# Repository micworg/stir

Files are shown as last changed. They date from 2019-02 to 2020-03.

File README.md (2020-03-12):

# Dual magnetic stir controller V2

## Overview

This is the Arduino project to build a double magnetic stirrer based on 2 fans, a 1602 LCD display, a KY-040 encoder and an Arduino Nano and a special PCB designed in the Hobbybrauer-Forum.

<p align="center">
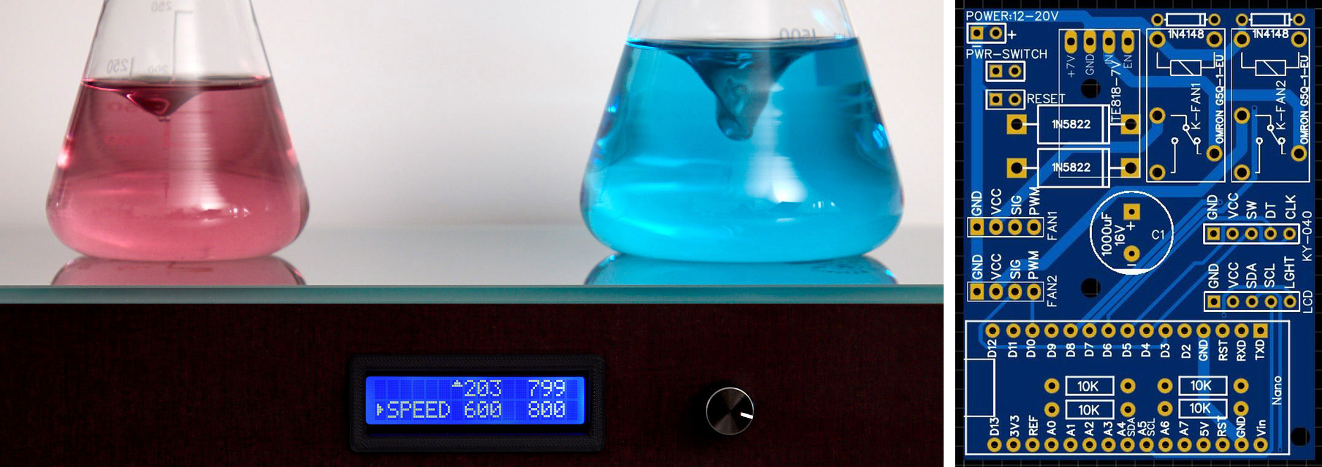
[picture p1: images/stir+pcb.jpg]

</p>

V2 supports dual voltage for the fans which increases the speed range.

In order to put the stirrer into operation you have to change the settings in stir.ino according to your setup (see below).

The stir V2 software is compatible with V1 hardware if you have used neither the RS232 Api nor the OFF0 and OFF1 relais pins.

## Part List

* 1x PCB "Stir V2.0"
* 1x Arduino Nano V3
* 1x [Voltage regulator TE818 5-24V to 5V 3A step down buck converter](https://www.ebay.de/itm/5x-Voltage-Regulator-5-24V-to-5V-3A-Step-Down-Buck-Converter-Power-Module-TE818/133109140535?ssPageName=STRK%3AMEBIDX%3AIT&_trksid=p2057872.m2749.l2649)
* 2x [Relais Omron G5Q-1-EU 5DC switching printrelais 5 V/DC 5A](https://www.conrad.de/de/p/omron-g5q-1-eu-5dc-printrelais-5-v-dc-5-a-1-wechsler-1-st-503930.html)
* 2x [Diode 1N4148 Diotec](https://www.conrad.de/de/p/stmicroelectronics-schottky-diode-gleichrichter-1n5822-do-201ad-40-v-einzeln-168275.html)
* 1x [Electrolytic capacitor 1000µF/16V Yageo SE016M1000B5S-1015](https://www.conrad.de/de/p/yageo-se016m1000b5s-1015-elektrolyt-kondensator-radial-bedrahtet-5-mm-1000-f-16-v-20-x-h-10-mm-x-15-mm-1-st-445386.html)
* 2x [Diode 1N5822 STMicroelectronics Schottky-Diode](https://www.conrad.de/de/p/diotec-ultraschnelle-si-diode-1n4148-sod-27-75-v-150-ma-162280.html)
* 4x [Metal film resistor 10 KOhm 0,6 W](https://www.conrad.de/de/p/rs-pro-metallschichtwiderstand-10k-0-5-0-6w-807200469.html)
* 2x Fan BeQuiet SilentWings 3 120mm PWM Highspeed or Noctua NF-R8 Redux-1800 80mm PWM
* 1x Power supply 12V-16V DC / 2A
* 1x Built-in socket for plug-in power supply unit
* 1x I2C 16x2 Arduino LCD Display Module
* 1x [Rotary encoder KY-040](https://www.conrad.de/de/p/joy-it-kodierter-drehschalter-rotary-encoder-1695709.html)
* 2x Magnet mount (3D printed)
* 4x Neodymium magnet 20x10 mm (N52, 1 oder 2 mm dick)

In addition, a housing is required that can be individually designed according to possibilities and capabilities.

<p align="center">
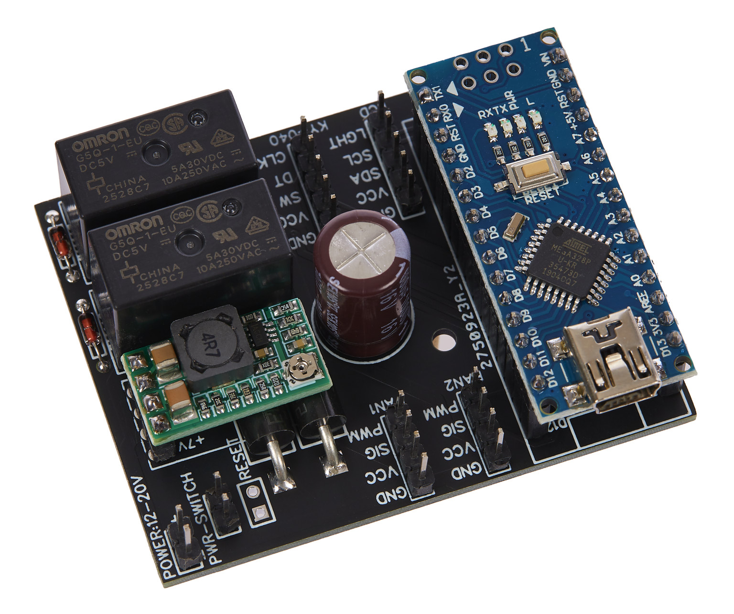
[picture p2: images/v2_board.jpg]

</p>

## Reference

This project was created based on an idea from the german Hobbybrauer-Forum and would not be possible without the ideas from there.

The forum: https://hobbybrauer.de/

The thread: https://hobbybrauer.de/forum/viewtopic.php?f=21&t=1456

Special thanks for development and testing:

* Herbert Schmid 
* Adrian Sigel
* Jens Warkentin
* Bastian Werner

## Overview of Functions

All functions are controlled by the KY-040 encoder:

* **Short Press:** change between menu, stirrer 1 and stirrer 2
* **Turn when menu is selected**: change between menu items (SPEED, BOOST, BTIME, CATCH, CTIME)
* **Long press when menu is selected**: lock all functions (unlock also by long press)
* **When a stirrer is selected**:
  * **SPEED**: turn sets speed, long press switches stirrer on or off.
  * **BOOST**: turn sets boost speed, long press activates/deactivates the boost function (running time is shown in the display).
  * **BTIME**: turn changes the boost time in minutes.
  * **CATCH**: turn activates/deactivates the fishing function
  * **CTIME**: turn changes the interval in minutes for the fish catching function
  * **RTIME**: turn changes speed rise time in seconds (applies to power on, stirrer on, boost on and fish catching)
  * **OTIME**: turn changes switch off time in hours (the timer activates immediately, 0 = switch off disabled)
  * **RNVAL**: random value range (a random values in this range will be added to speed) 
* **Other menu options**:
  * **CFG**: Configuration menu 

Functions in the congirutation sub menu
* **Short Press**: switch between config option and and value.
* **Long press**: exit configuration menu.
* **Turn**: select configuration option or change value.

## Display Indicators:

* **Bottom Left**: Menu
* **Bottom Center/Right**: displays the set values for the stirrers depending on the selected menu item.
* **Top Center/Right**: displays the current stirrer speed (or 'OFF' or 'CAT' (Fishing)).
* **Top Left**: shows the remaining time of the boost or switch off function.

## Settings (in stir.ino)

|Value|Config|Description|
|:----------------|:-----|:----------|
|`LGHT`           |`LGHT`|LCD display brightness|
|`SPEEDINC1`      |`SPI1`|increment of speed values when turning the encoder (1. range)|
|`SPEEDINC2`      |`SPI2`|increment of speed values when turning the encoder (2. range)|
|`SPEEDINC3`      |`SPI3`|increment of speed values when turning the encoder (3. range)|
|`SPEEDSTEP1`     |`SPS1`|speed increment steps (increment changes at these values, separates range 1 and 2)|
|`SPEEDSTEP2`     |`SPS2`|speed increment steps (increment changes at these values, separates range 2 and 3))|
|`FANMIN`         |`FMIN`|fan minimum speed (should be a value at which the fan runs safely) (rpm)|
|`FANMAX`         |`FMAX`|fan maximum speed  (it's important that this is the real maximum value of the fan) (rpm)|
|`FANINIT`        |`FINI`|set fans to high voltage for 3 sec at boot (0/1)|
|`BOFF`           |`BOFF`|if set boost off will also turn the normal mode off (0/1)|
|`BINC`           |`BINC`|boost time increment (min)|
|`CINC`           |`CINC`|catch time increment (min)|
|`RINC`           |`RINC`|rise time increment (sec)|
|`OINC`           |`OINC`|off timer increment (hour)|
|`RNDINC`         |`RINC`|randon value increment (rpm)|
|`CATCHSTOP`      |`CSTP`|stop interval for stir fish catch function (ms)|
|`PWM0`, `PWM1`   |      |PWM output pins for fan speed|
|`PWM2`           |      |PWM output pin for LCD brightness control|
|`I0`, `I1`       |      |interrupts for rpm measurement (0/1 for Uno/Nano, 2/3 for Leonardo/ProMicro)|
|`SWAPENC`        |`SWEN`|switch KY-040 encoder direxction (0/1)| 
|`CLK`, `DT`, `SW`|      |pins for KY-040 encoder| 
|`R0`, `R0`       |      |voltage select relais pin| 
|`RTHRES`         |`RTHR`|voltage switch threshold (rpm)| 
|`RINTERVAL`      |`XINT`|regulation interval (ms)|
|`RDELAY`         |`XDEL`|extra regulation delay when value changes (ms)|
|`RTOL`           |`XTOL`|regulation tolerance (rpm)|
|`RNDINTERVL`     |`RINT`|randon value range change interval (ms)|
|`SINTERVAL`      |`SINT`|speed measurement interval (ms)|
|`SAVERAGE`       |`SAVG`|speed measurement average|
|`SAVETAG`        |      |parameter save identifier|
|`SAVEDELAY`      |      |delay in seconds before parameter will be saved to EEPROM|
|`LCDB`           |      |LCD brightness steps (10 values, 0=off, 255=max)|
|`RESET`          |`RSET`|change this value in configuration menu to 1 for factory reset|

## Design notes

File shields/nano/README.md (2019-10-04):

# Stir Shield

Stir shields for Arduino NANO from Jens Warkentin.

<p align="center">
<B>Gerber_Stir.Nano+StepDown.V3_.zip<B><BR>
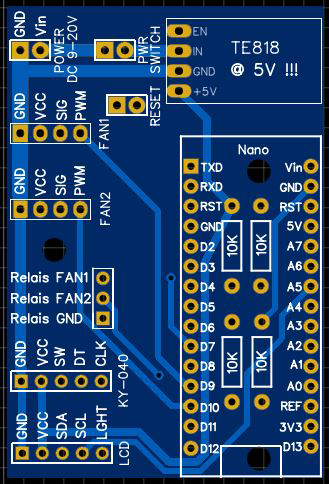
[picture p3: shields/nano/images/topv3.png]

</p>

<p align="center">
<B>Gerber_Stir_Arduino_Nano.zip<B><BR>
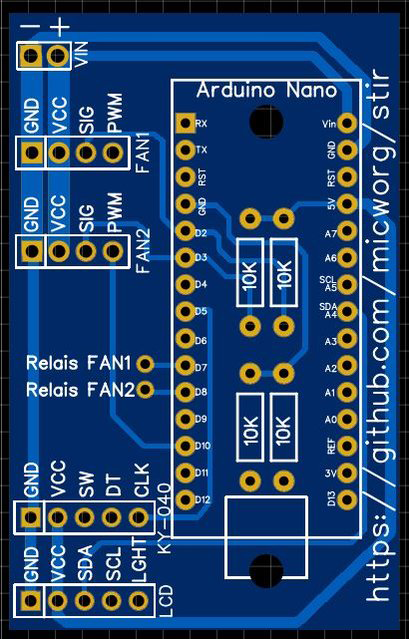
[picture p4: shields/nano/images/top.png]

</p>

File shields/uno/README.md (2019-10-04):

# Stir Shield

Stir shield for Arduino UNO from Adrian Sigel.

<p align="center">
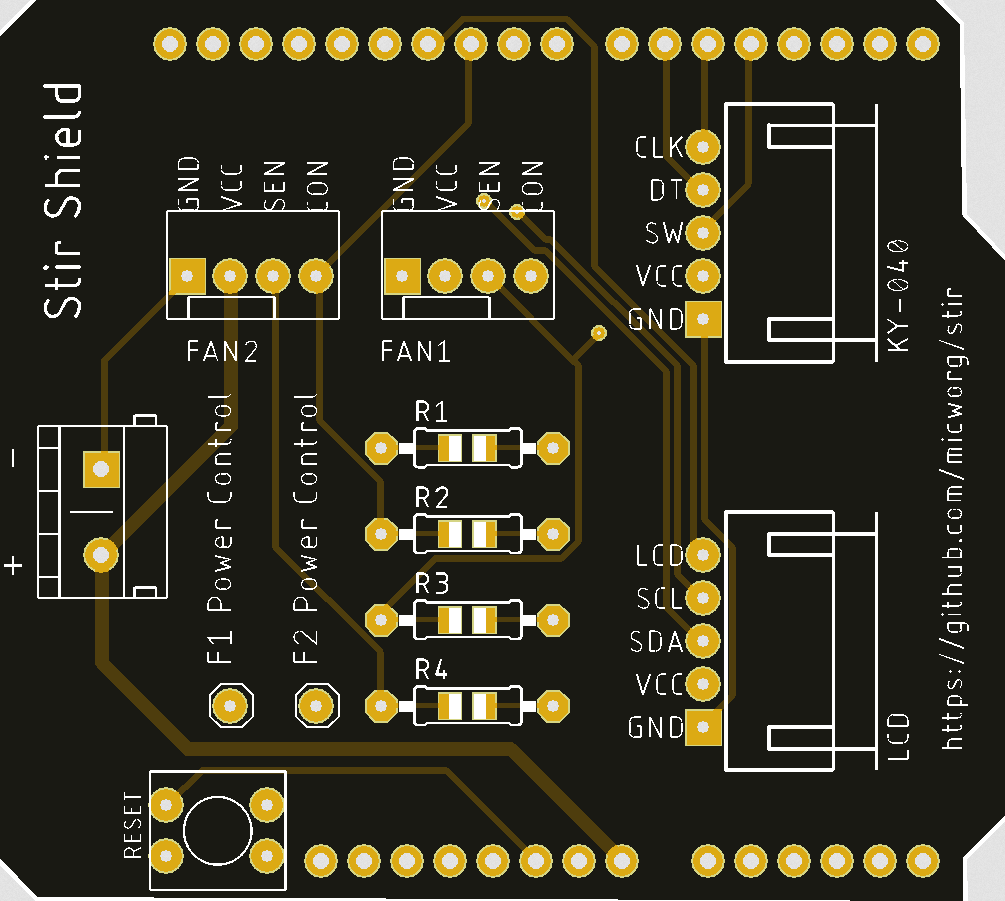
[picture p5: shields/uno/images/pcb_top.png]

</p>

<p align="center">
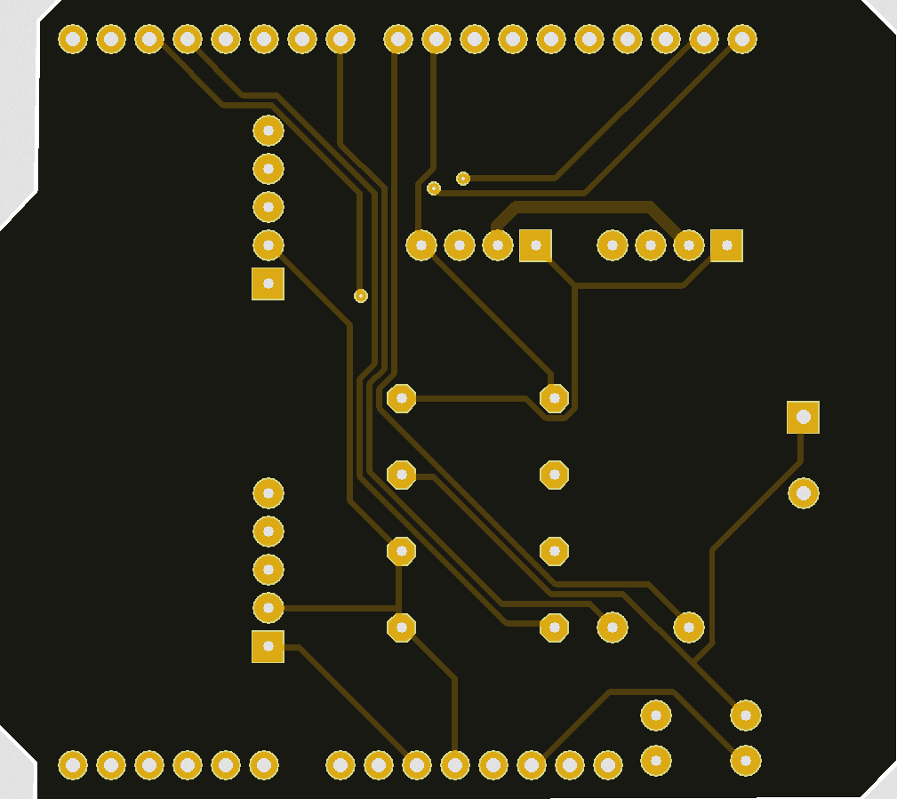
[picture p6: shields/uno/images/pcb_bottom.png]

</p>

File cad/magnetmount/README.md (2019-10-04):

# CAD Files

CAD files for 3D printed magnet moun. Compatible for magnets with size 20x10x5 mm and 
*be quiet! Silent Wings 3 120/140 mm* fans.

<p align="center">
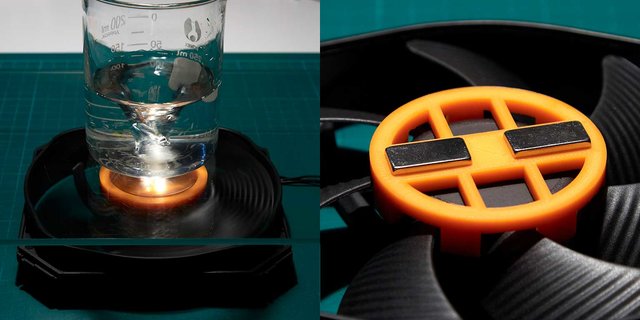
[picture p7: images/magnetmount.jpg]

</p>

<p align="center">
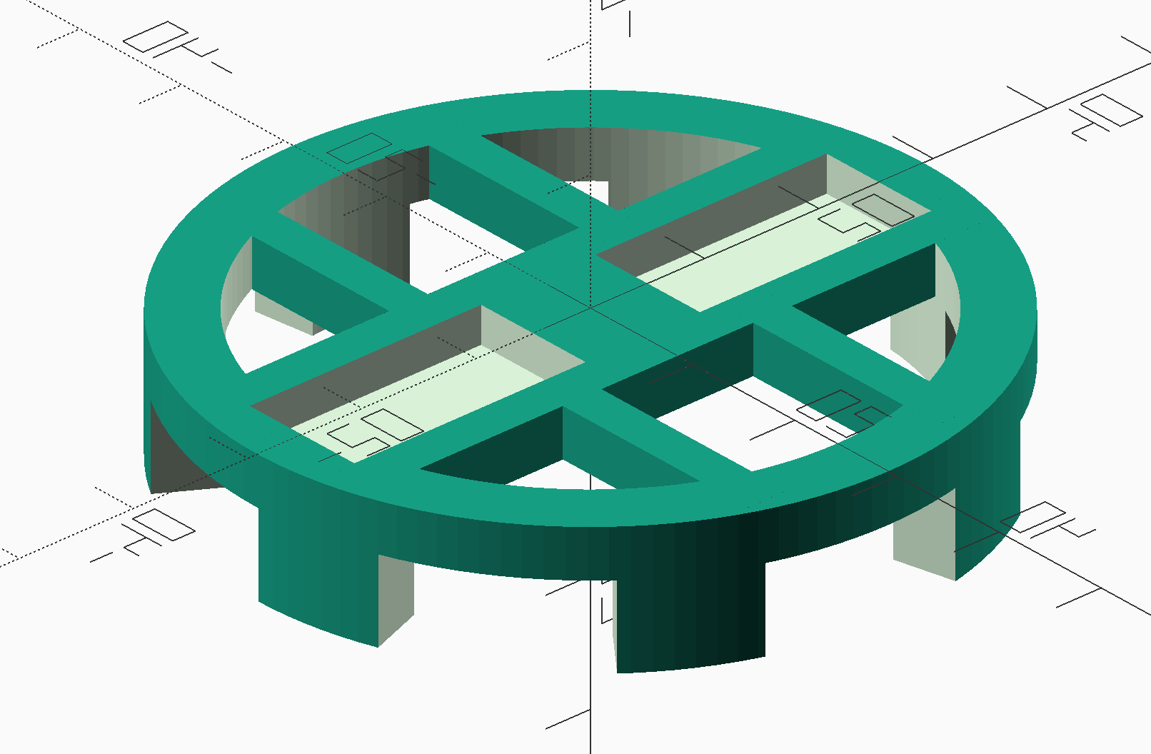
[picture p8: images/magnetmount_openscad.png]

</p>

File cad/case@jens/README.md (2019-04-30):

# CAD Files

CAD files for 3D printed case parts from Jens Warkentin.

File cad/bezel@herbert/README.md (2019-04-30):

# CAD Files

CAD files for 3D printed display bezel from Herbert Schmid.

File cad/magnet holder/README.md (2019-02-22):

# CAD Files

CAD files for 3D printed magnet holder. Compatible for magnets with size 20x10x5 mm and 
*be quiet! Silent Wings 3 140 mm* fans.

<p align="center">

</p>

<p align="center">

</p>

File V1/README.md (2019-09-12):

# Dual magnetic stir controller

## Overview

This is the Arduino sketch to build a double magnetic stirrer based on 2 fans, a 1602 LCD display, a KY-040 encoder and an Arduino (e.g. Uno, Nano, Leonardo, Pro Micro).

<p align="center">
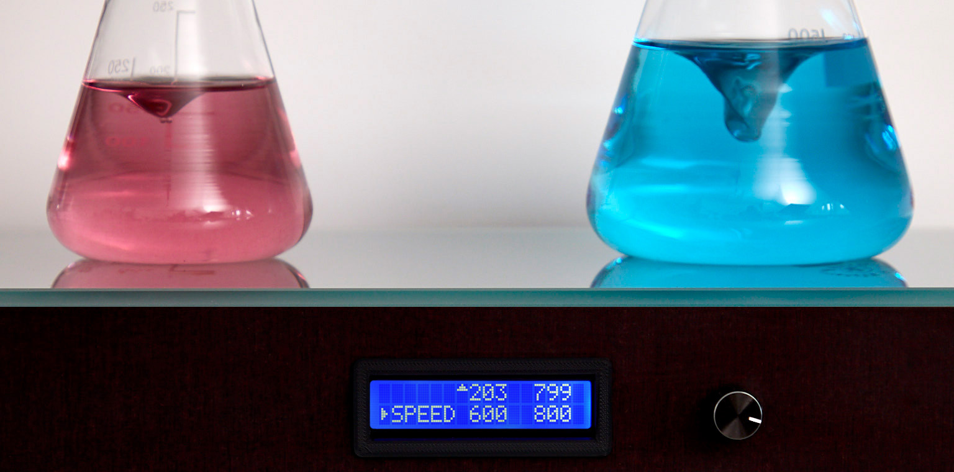
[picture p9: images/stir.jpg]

</p>

In order to put the stirrer into operation you have to change the settings in stir.ino according to your setup.

## Reference

This project was created based on an idea from the Hobbybrauer-Forum and would not be possible without the ideas from there.

The forum: https://hobbybrauer.de/

The thread: https://hobbybrauer.de/forum/viewtopic.php?f=21&t=1456

## Overview of Functions

All functions are controlled by the KY-040 encoder:

* **Short Press:** change between menu, stirrer 1 and stirrer 2
* **Turn when menu is selected**: change between menu items (SPEED, BOOST, BTIME, CATCH, CTIME)
* **Long press when menu is selected**: lock all functions (unlock also by long press)
* **When a stirrer is selected**:
  * **SPEED**: turn sets speed, long press switches stirrer on or off.
  * **BOOST**: turn sets boost speed, long press activates/deactivates the boost function (running time is shown in the display).
  * **BTIME**: turn changes the boost time in minutes.
  * **CATCH**: turn activates/deactivates the fishing function
  * **CTIME**: turn changes the interval in minutes for the fish catching function
  * **RTIME**: turn changes speed rise time in seconds (applies to power on, stirrer on, boost on and fish catching)
  * **OTIME**: turn changes switch off time in hours (the timer activates immediately, 0 = switch off disabled)
  * **RNVAL**: random value range (a random values in this range will be added to speed) 
* **Other menu options**:
  * **BRGHT**: LCD brightness

## Display Indicators:

* **Bottom Left**: Menu
* **Bottom Center/Right**: displays the set values for the stirrers depending on the selected menu item.
* **Top Center/Right**: displays the current stirrer speed (or 'OFF' or 'CAT' (Fishing)).
* **Top Left**: shows the remaining time of the boost or switch off function.

## Settings (in stir.ino)

|Value|Description|
|:----|:----------|
|`SPEEDINC`|increment of speed values when turning the encoder|
|`FANMIN`|fan minimum speed (should be a value at which the fan runs safely) (rpm)|
|`FANMAX`|maximum speed of the fan (it is important that this is the real maximum value of the fan) (rpm)|
|`BOFF`|if set boost off will also turn the normal mode off|
|`BINC`|boost time increment (min)|
|`CINC`|catch time increment (min)|
|`RINC`|rise time increment (sec)|
|`OINC`|off timer increment (hour)|
|`CATCHSTOP`|stop interval for stir fish catch function (ms)|
|`PWM0`, `PWM1`|PWM output pins for fan speed|
|`PWM2`|PWM output pin for LCD brightness control|
|`I0`, `I1`|interrupts for rpm measurement (2 and 3 for Leonardo and ProMicro / 0 and 1 for Uno)|
|`CLK`, `DT`, `SW`|pins for KY-040 encoder| 
|`OFF0`, `OFF1`|these pins will be set if the fan is off| 
|`OFFSTATE`|off state (LOW/HIGH)| 
|`RINTERVAL`|regulation interval (ms)|
|`RDELAY`|extra regulation delay when value changes (ms)|
|`RTOL`|regulation tolerance (rpm)|
|`RNDINTERVL`|randon value range change interval (ms)|
|`SINTERVAL`|speed measurement interval (ms)|
|`SAVERAGE`|speed measurement average|
|`SAVETAG`|parameter save identifier|
|`SAVEDELAY`|delay in seconds before parameter will be saved to EEPROM|
|`LCDB`|LCD brightness steps (10 values, 0=off, 255=max)|

## API commands

Commands are colon separated an can be send via USB/Serial

|Command|Description|
|:------|:----------|
|`info`|returns a colon separated string with all parameters (see below)|
|`version`|returns the software version|
|`on:<0/1>`|switch stirren on|
|`off:<0/1>`|switch stirren off|
|`bon:<0/1>`|switch boost mode on|
|`boff:<0/1>`|switch boost mode off|
|`speed:<0/1>:<rpm>`|set stirrer speed (FANMIN-FANMAX rpm)|
|`bspeed:<0/1>:<rpm>`|set stirrer boost speed (speed-FANMAX rpm)|
|`btime:<0/1>:<min>`|set boost time (0-60)|
|`con:<0/1>`|switch catch mode on|
|`coff:<0/1>`|switch catch mode off|
|`ctime:<0/1>:<min>`|set catch mode interval (60-240 min)|
|`rtime:<0/1>:<sec>`|set speed rise time (0-240 sec)|
|`rnval:<0/1>:<rpm>`|set randon value range (0-1000 rpm)|
|`otime:<0/1>:<hour>`|switch stirrer off after time in hours (1-99 hour, 0 deactivates switch off)|

All commands return a colon separated string with all current parameters:

|Element|Stirrer|Variable in stir.ino|Description|
|:------|:------|:-------------------|:----------|
| 0|0|`F[0]`     |state (0=on, 1=off)|
| 1|0|`v[0]`     |speed (rpm)|
| 2|0|`b[0]`     |boost speed (rpm)|
| 3|0|`rpm[0]`   |rpm|
| 4|0|`xpm[0]`   |averaged rpm|
| 5|0|`r[0]`     |regulation value|
| 6|0|`bstate[0]`|boost state (0=on, 1=off)|
| 7|0|`btime[0]` |boost time (min)|
| 8|0|`cat[0]`   |fish catch mode state (0=on, 1=off)|
| 9|0|`ctime[0]` |fish catch time interval (min)|
|10|0|`rtime[0]` |speed rise time (sec)|
|11|0|`otime[0]` |switch off time (hour)|
|12|0|`rnval[0]` |random value range (rpm)|
|13|0|`rnd[0]`   |current random value (rpm)|
|14|0|           |boost remain (sec)|
|15|0|           |off timer remain (sec)|
|16|1|`F[1]`     |state (0=on, 1=off)|
|17|1|`v[1]`     |speed (rpm)|
|18|1|`b[1]`     |boost speed (rpm)|
|19|1|`rpm[1]`   |rpm|
|20|1|`xpm[1]`   |averaged rpm|
|21|1|`r[1]`     |regulation value|
|22|1|`bstate[1]`|boost state (0=on, 1=off)|
|23|1|`btime[1]` |boost time (min)|
|24|1|`cat[1]`   |fish catch mode state (0=on, 1=off)|
|25|1|`ctime[1]` |fish catch time interval (min)|
|26|1|`rtime[1]` |speed rise time (sec)|
|27|1|`otime[1]` |switch off time (hour)|
|28|1|`rnval[1]` |random value range (rpm)|
|29|1|`rnd[1]`   |current random value (rpm)|
|30|1|           |boost remain (sec)|
|31|1|           |off timer remain (sec)|
|32| |           |software version|
|33| |           |uptime (ms)|
|34| |           |0=ok, 1=error|

## Schematics

<p align="center">
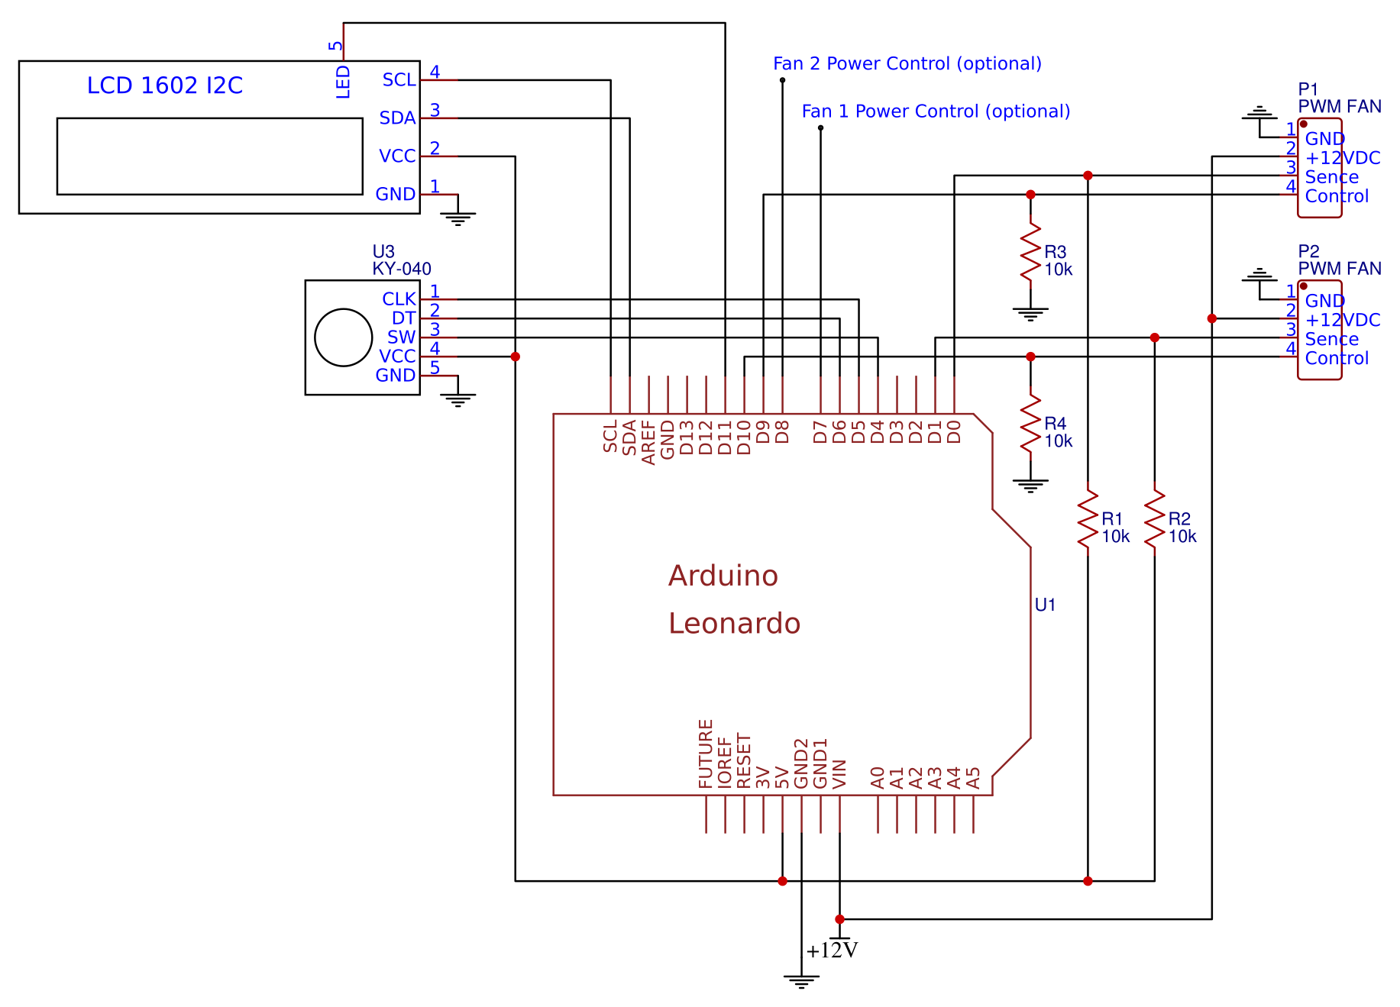
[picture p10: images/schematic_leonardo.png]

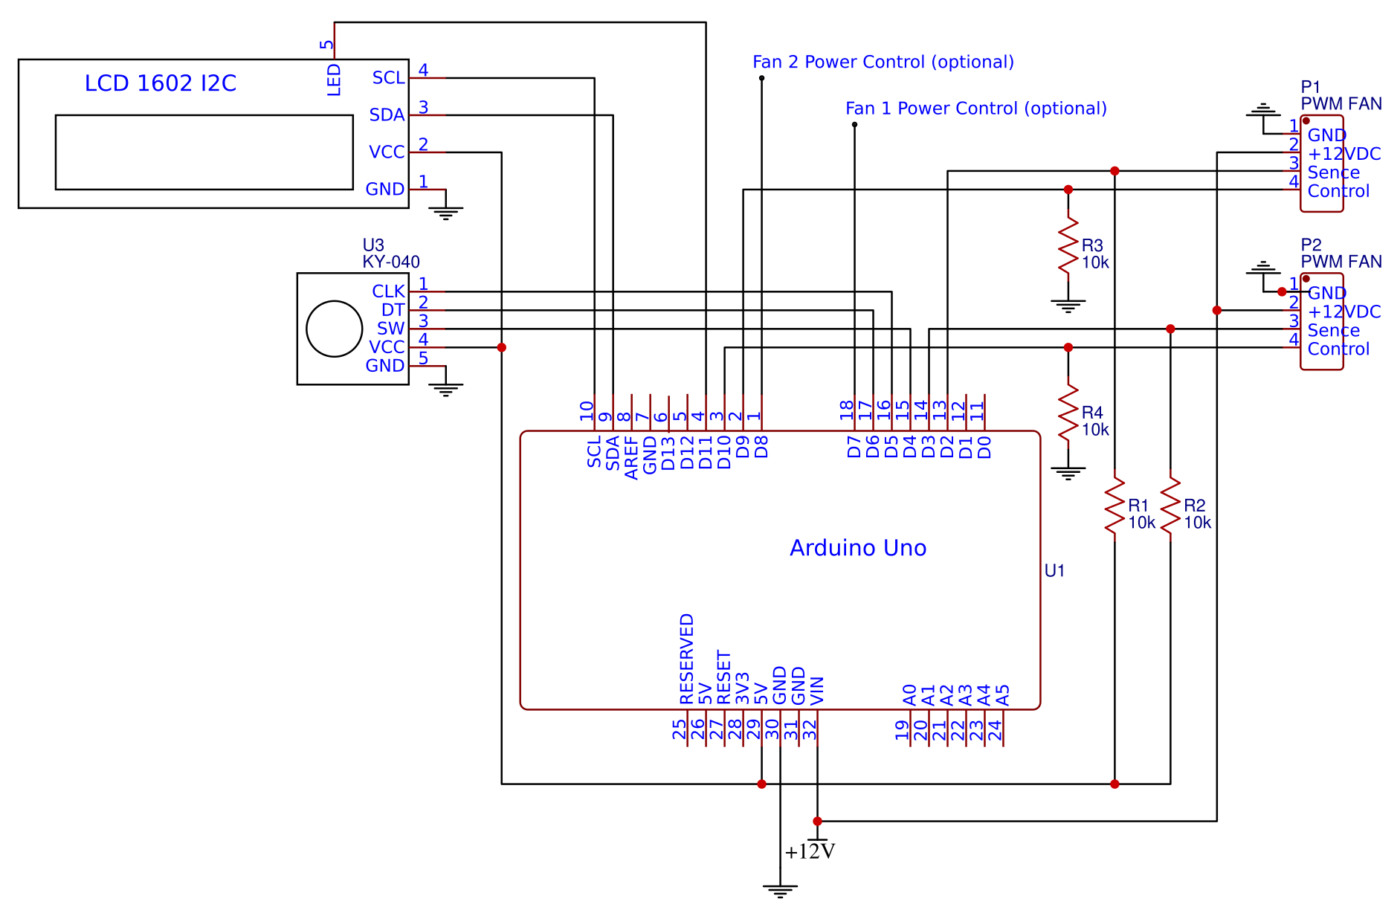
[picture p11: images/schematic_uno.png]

</p>

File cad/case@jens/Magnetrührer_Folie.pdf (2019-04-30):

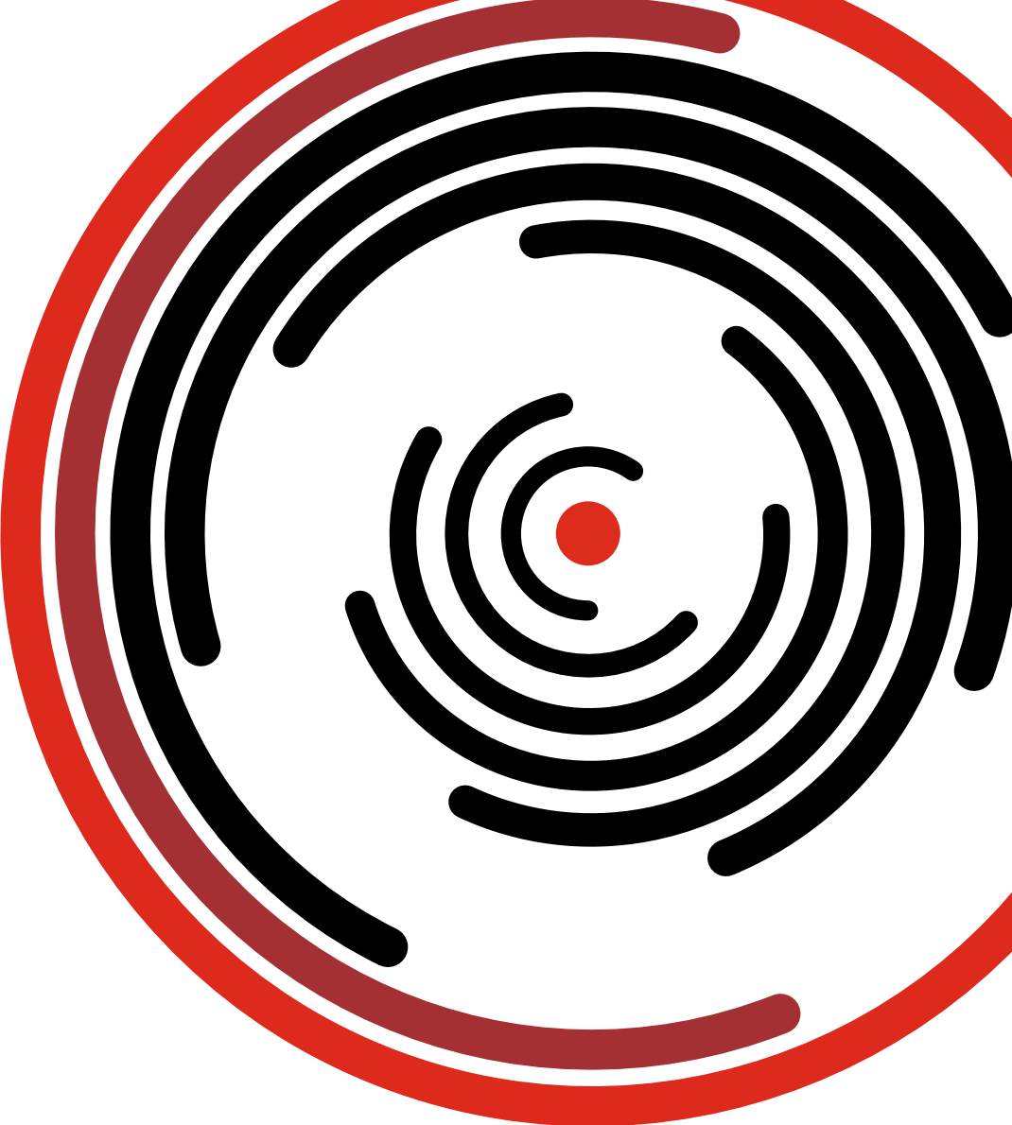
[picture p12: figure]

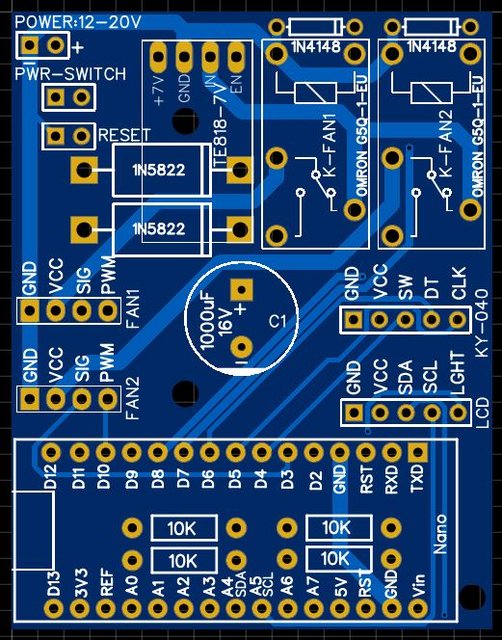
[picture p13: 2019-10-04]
images/pcb_top.jpg

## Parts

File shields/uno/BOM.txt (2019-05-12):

Power Input:

1x KF301-2P screw terminal => https://de.aliexpress.com/item/20-teile-los-KF301-2P-KF301-5-0-2P-KF301-Schraube-2Pin-5-0mm-Gerade-Pin/32867190033.html?spm=a2g0x.search0104.3.1.2c912b5fntkTJD&ws_ab_test=searchweb0_0%2Csearchweb201602_10_10065_10068_319_10059_10884_317_10887_10696_321_322_10084_453_10083_454_10103_10618_10307_537_536_10134%2Csearchweb201603_52%2CppcSwitch_0&algo_pvid=18c869a1-9cc5-4b81-88bd-10d4c096c0ee&algo_expid=18c869a1-9cc5-4b81-88bd-10d4c096c0ee-0

Fan:

2x 2,54mm KF2510 3 + 1 P Straight => https://de.aliexpress.com/item/50-teile-los-2-54mm-KF2510-3-1-P-KF2510-4AW-m-nnlich-weibliche-geh-use/32961935772.html?spm=a2g0x.search0104.3.1.5d447ae1Nki8jb&ws_ab_test=searchweb0_0%2Csearchweb201602_10_10065_10068_319_10059_10884_317_10887_10696_321_322_10084_453_10083_454_10103_10618_10307_537_536_10134%2Csearchweb201603_52%2CppcSwitch_0&algo_pvid=cbe6ff59-92a1-432d-8c5c-8c9c7732600b&algo_expid=cbe6ff59-92a1-432d-8c5c-8c9c7732600b-0
2x 2.54mm Pin header male => https://de.aliexpress.com/item/10-st-cke-40Pin-2-54mm-Gerade-Einreihige-M-nnlichen-Pin-Header-Stecker-Streifen-PBC-DIY/32878749052.html?spm=a2g0x.search0104.3.85.48754ae7pld96U&ws_ab_test=searchweb0_0%2Csearchweb201602_10_10065_10068_319_10059_10884_317_10887_10696_321_322_10084_453_10083_454_10103_10618_10307_537_536_10134%2Csearchweb201603_52%2CppcSwitch_0&algo_pvid=6d1373ff-487b-4174-b289-f2b8f8d6dcd0&algo_expid=6d1373ff-487b-4174-b289-f2b8f8d6dcd0-12

Reset:

1x Micro pressure switch => https://de.aliexpress.com/item/100-teile-los-Mini-Micro-Momentary-Taktile-Druckschalter-6-6-5mm-4-pin-ON-OFF-tasten/32858344336.html?spm=a2g0x.search0104.3.43.3aa022bdWBlQ8n&ws_ab_test=searchweb0_0%2Csearchweb201602_10_10065_10068_319_10059_10884_317_10887_10696_321_322_10084_453_10083_454_10103_10618_10307_537_536_10134%2Csearchweb201603_52%2CppcSwitch_0&algo_pvid=2cb51b61-71a9-4cec-b3bf-494134fa318e&algo_expid=2cb51b61-71a9-4cec-b3bf-494134fa318e-6

Output's:

2x XH2.54 square male 5P => https://de.aliexpress.com/item/50PCS-Lot-XH2-54-Right-Angle-Pin-Header-Connector-2P-3P-4P-5P-6P-7P-8P/32822859426.html?spm=a2g0x.search0104.3.8.d58e3f185YK9t8&ws_ab_test=searchweb0_0,searchweb201602_10_10065_10068_319_10059_10884_317_10887_10696_321_322_10084_453_10083_454_10103_10618_10307_537_536_10134,searchweb201603_52,ppcSwitch_0&algo_expid=9f565a80-ffcb-40ff-a45a-78ad388fbc3b-1&algo_pvid=9f565a80-ffcb-40ff-a45a-78ad388fbc3b
2x XH2.54 female 5P => https://de.aliexpress.com/item/10PCS-XH2-54-2P-3P-3P-4P-5P-6P-7P-8P-9P-10P-11P-12P-Pitch/32771742483.html?spm=a2g0x.search0104.3.304.643773f2xd0Fnr&ws_ab_test=searchweb0_0,searchweb201602_10_10065_10068_319_10059_10884_317_10887_10696_321_322_10084_453_10083_454_10103_10618_10307_537_536_10134,searchweb201603_52,ppcSwitch_0&algo_expid=ff250363-7f23-4460-b86f-a25e39925240-43&algo_pvid=ff250363-7f23-4460-b86f-a25e39925240

Resistors:

4x 10 kOhm SMD or THT Resistors => 
https://de.aliexpress.com/item/100-st-cke-0805-5-1-8-watt-SMD-chip-widerstand-0R-10-mt-0-1R/32865947306.html?spm=a2g0x.search0104.3.2.3e337801L8ie9i&ws_ab_test=searchweb0_0%2Csearchweb201602_10_10065_10068_319_10059_10884_317_10887_10696_321_322_10084_453_10083_454_10103_10618_10307_537_536_10134%2Csearchweb201603_52%2CppcSwitch_0&algo_pvid=771d229c-6332-4f9b-86f8-d9c456937ff3&algo_expid=771d229c-6332-4f9b-86f8-d9c456937ff3-0
https://de.aliexpress.com/item/100-st-cke-1-4-watt-Metall-Film-Widerstand-0-25-watt-1-0-2-2/32952777282.html?spm=a2g0x.search0104.3.16.5e9c112fwd3FS3&ws_ab_test=searchweb0_0%2Csearchweb201602_10_10065_10068_319_10059_10884_317_10887_10696_321_322_10084_453_10083_454_10103_10618_10307_537_536_10134%2Csearchweb201603_52%2CppcSwitch_0&algo_pvid=9573d819-3d0b-4108-9ac4-c8d4065f59a4&algo_expid=9573d819-3d0b-4108-9ac4-c8d4065f59a4-2

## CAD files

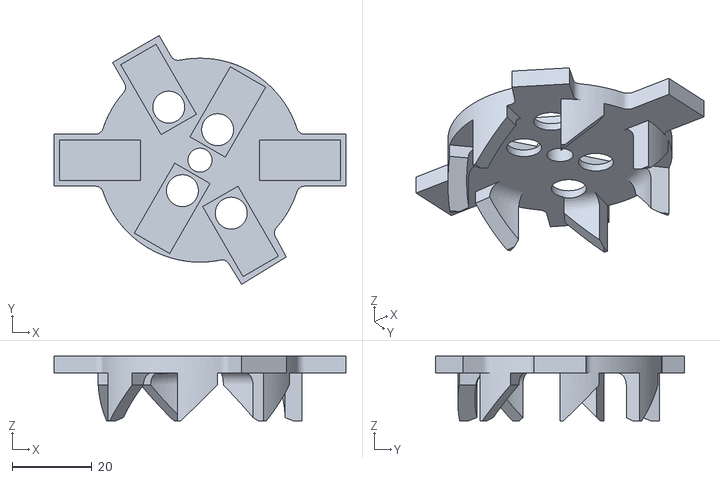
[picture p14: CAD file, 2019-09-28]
cad/bezel@herbert/Magnetaufnahme Rührer Wing3_V2.0.stl
73.0 x 62.2 x 16.2

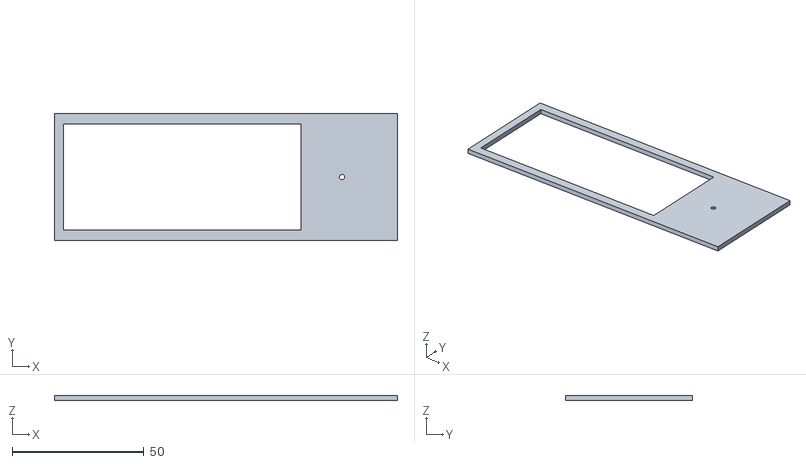
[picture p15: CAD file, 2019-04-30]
cad/case@jens/Bohrschablone_LCD Blende.stl
130.0 x 48.0 x 2.00

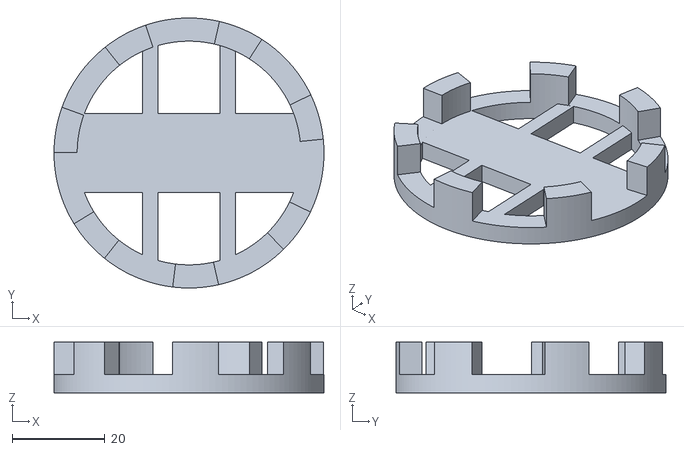
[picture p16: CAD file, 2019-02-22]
cad/magnetmount.stl
58.3 x 58.3 x 11.0

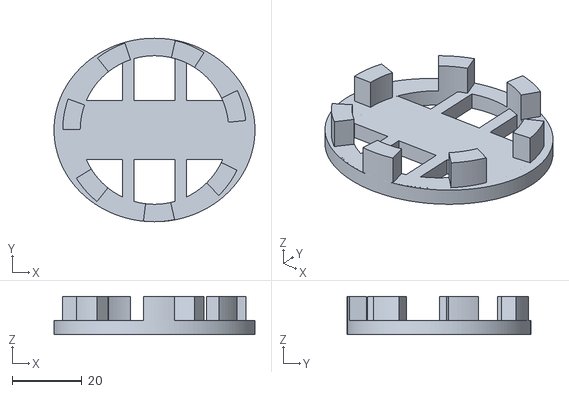
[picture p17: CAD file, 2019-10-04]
cad/magnetmount/magnetmount120x10.stl
57.5 x 52.5 x 11.0

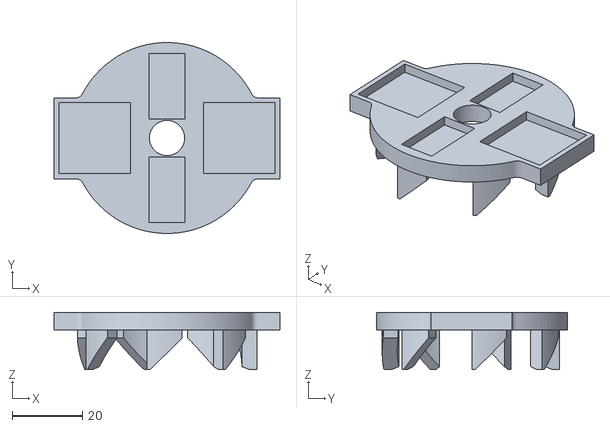
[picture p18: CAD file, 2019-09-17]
cad/bezel@herbert/Magnetaufnahme Rührer Wing3_V3.0.stl
64.2 x 54.2 x 16.2

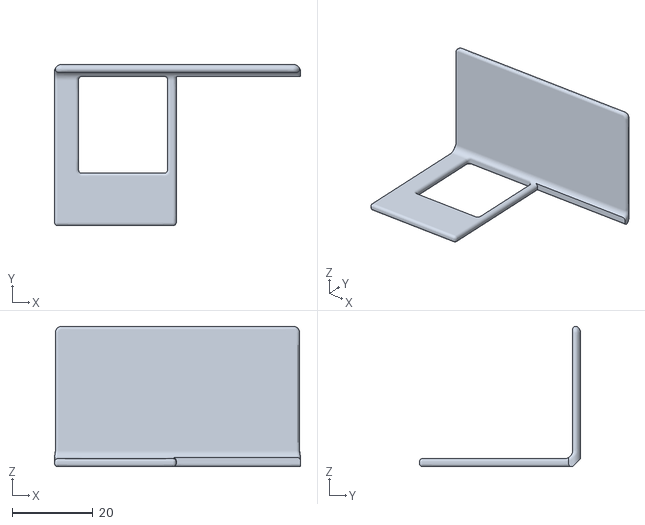
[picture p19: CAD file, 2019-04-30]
cad/case@jens/Frontblende.stl
61.0 x 40.0 x 34.8

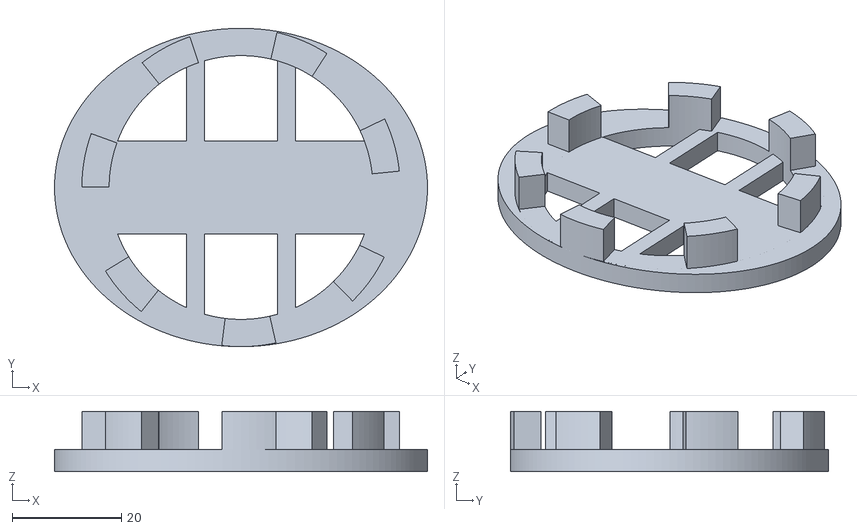
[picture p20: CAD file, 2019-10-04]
cad/magnetmount/magnetmount140x20.stl
68.3 x 58.3 x 11.0

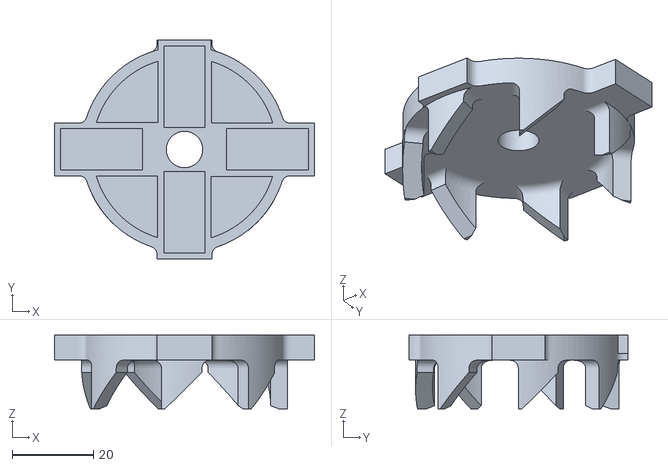
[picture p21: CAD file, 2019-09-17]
cad/bezel@herbert/Magnetaufnahme Rührer Wing3_V4.0.stl
64.2 x 54.0 x 18.2

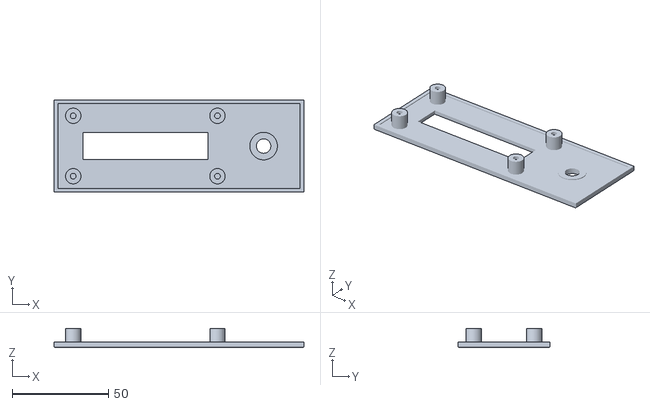
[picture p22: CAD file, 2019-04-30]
cad/case@jens/LCD+KY040_Blende.stl
130.0 x 48.0 x 10.0

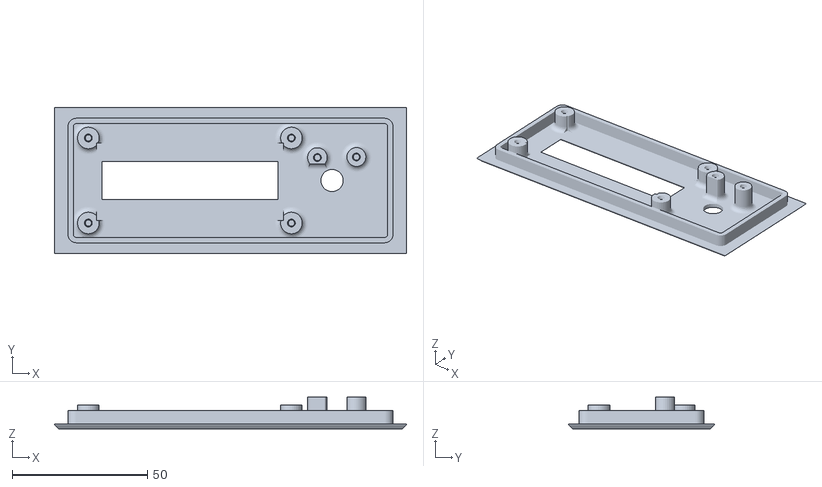
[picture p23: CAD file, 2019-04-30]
cad/bezel@herbert/LCD 1602_Blende mit Rahmen_Encoder links.stl
130.0 x 54.0 x 11.7

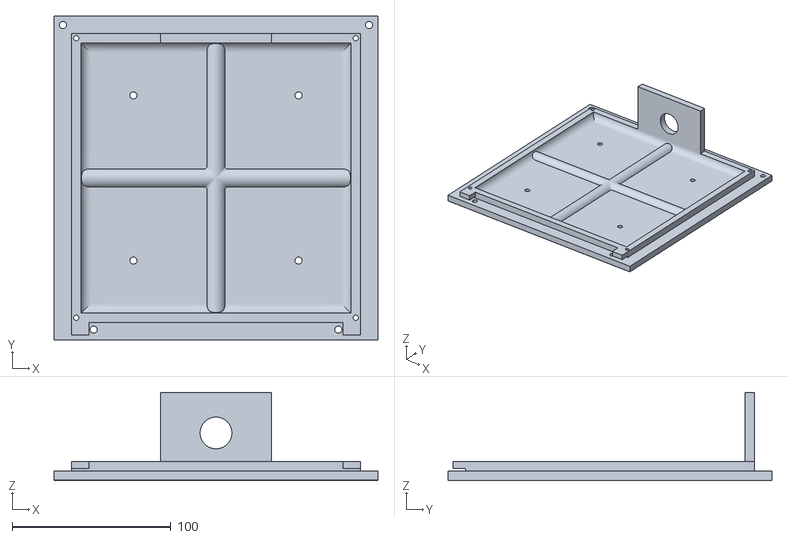
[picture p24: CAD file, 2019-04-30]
cad/case@jens/Bodenplatte_V1.1.stl
204.0 x 204.0 x 55.5

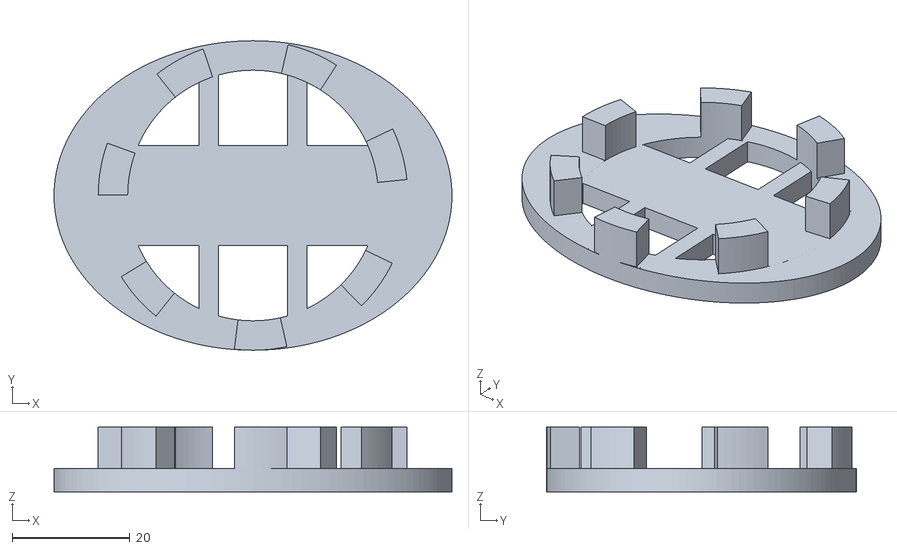
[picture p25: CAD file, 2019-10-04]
cad/magnetmount/magnetmount120x20.stl
67.5 x 52.5 x 11.0

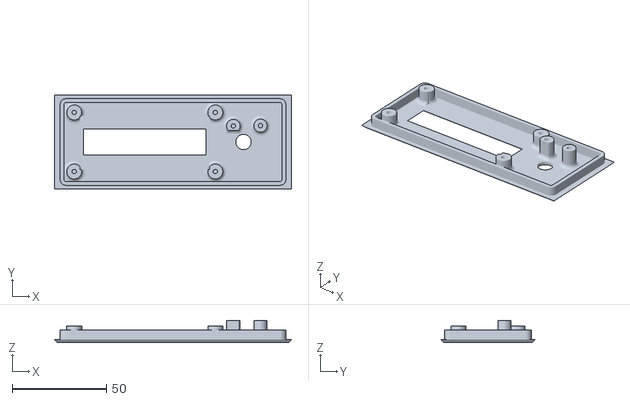
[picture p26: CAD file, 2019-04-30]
cad/bezel@herbert/LCD 1602_Blende mit Rahmen_Encoder links_50mm.stl
126.0 x 50.0 x 11.7

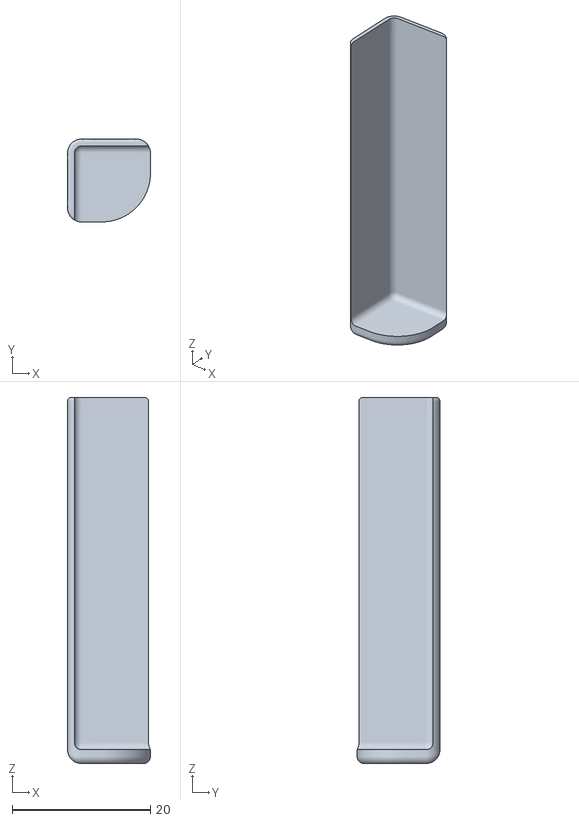
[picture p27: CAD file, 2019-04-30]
cad/case@jens/Kantenschutz.stl
12.0 x 12.0 x 53.0

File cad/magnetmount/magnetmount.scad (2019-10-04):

/// magnet mount for for magnets with size 20x10x5 mm and be quiet! Silent Wings 3 120/140 mm fans

$fn=128;

g   = 10;     // magnet gap
fan = 120;    // fan size (120 or 140)

h   = 4;      // base height
r   = 5;      // edge width

pn  = 7;      // number of pins
ph  = 7;      // pin height
pa  = 20;     // pin angle

mw  = 10.25;  // magnet width
ml  = 20.25;  // magnet length
mb  = 17;     // magnet bar width

fw= fan==140 ? 48.3 : 42.5; // fan center width
eo= fan==140 ? 10   : 5;    // elliptic extra offset

d=fw+r+r;     // total diameter
cl=d-r;       // magnet bar length
a=360/pn;     // segment angle
e=(d+g-eo)/d; // elliptic scale factor


difference() {
  union() {
    difference() {
      union() {
      translate([0,0,0]) cylinder(h+ph,d/2,d/2);
      translate([0,0,0]) scale([e, 1, 1]) cylinder(h,d/2,d/2);
      }
      translate([0,0,-1]) cylinder(h+ph+2,d/2-r,d/2-r);
      for (i =[0:1:pn-1]) {
        pin(a*i);
      }
    }
    translate([-cl/2,-mb/2,0]) cube([cl,mb,h]);
    rotate ([0,0,90]) translate([-cl/2,-(mb-mw)/4-d/7,0]) cube([cl,(mb-mw)/2,h]);
    rotate ([0,0,90]) translate([-cl/2,-(mb-mw)/4+d/7,0]) cube([cl,(mb-mw)/2,h]);
  }
  translate([-ml-g/2,-mw/2,-1]) cube([ml,mw,h]);
  translate([g/2,-mw/2,-1]) cube([ml,mw,h]);
}

module pin(r) {
  translate([0,0,0.01]) rotate([0,0,r]) hull() {
    translate([0,0,h]) cylinder(h+ph,0.1,0.1);
    translate([-d,0,h]) cylinder(h+ph,0.1,0.1);
    rotate ([0,0,a-pa])union() {
      translate([0,0,h]) cylinder(h+ph,0.1,0.1);
      translate([-d,0,h]) cylinder(h+ph,0.1,0.1);
    }
  }
}

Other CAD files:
cad/magnetmount/magnetmount140x10.stl
cad/bezel@herbert/LCD -Einbaurahmen für Blende mit Encoder.stl
cad/case@jens/KY040_Knopf.stl
cad/bezel@herbert/LCD -Einbaurahmen für Blende mit Encoder_50 mm.stl
cad/bezel@herbert/LCD 1602_Blende mit Rahmen_Encoder.stl
cad/bezel@herbert/OLED-Blende_Encoder_neutral.stl

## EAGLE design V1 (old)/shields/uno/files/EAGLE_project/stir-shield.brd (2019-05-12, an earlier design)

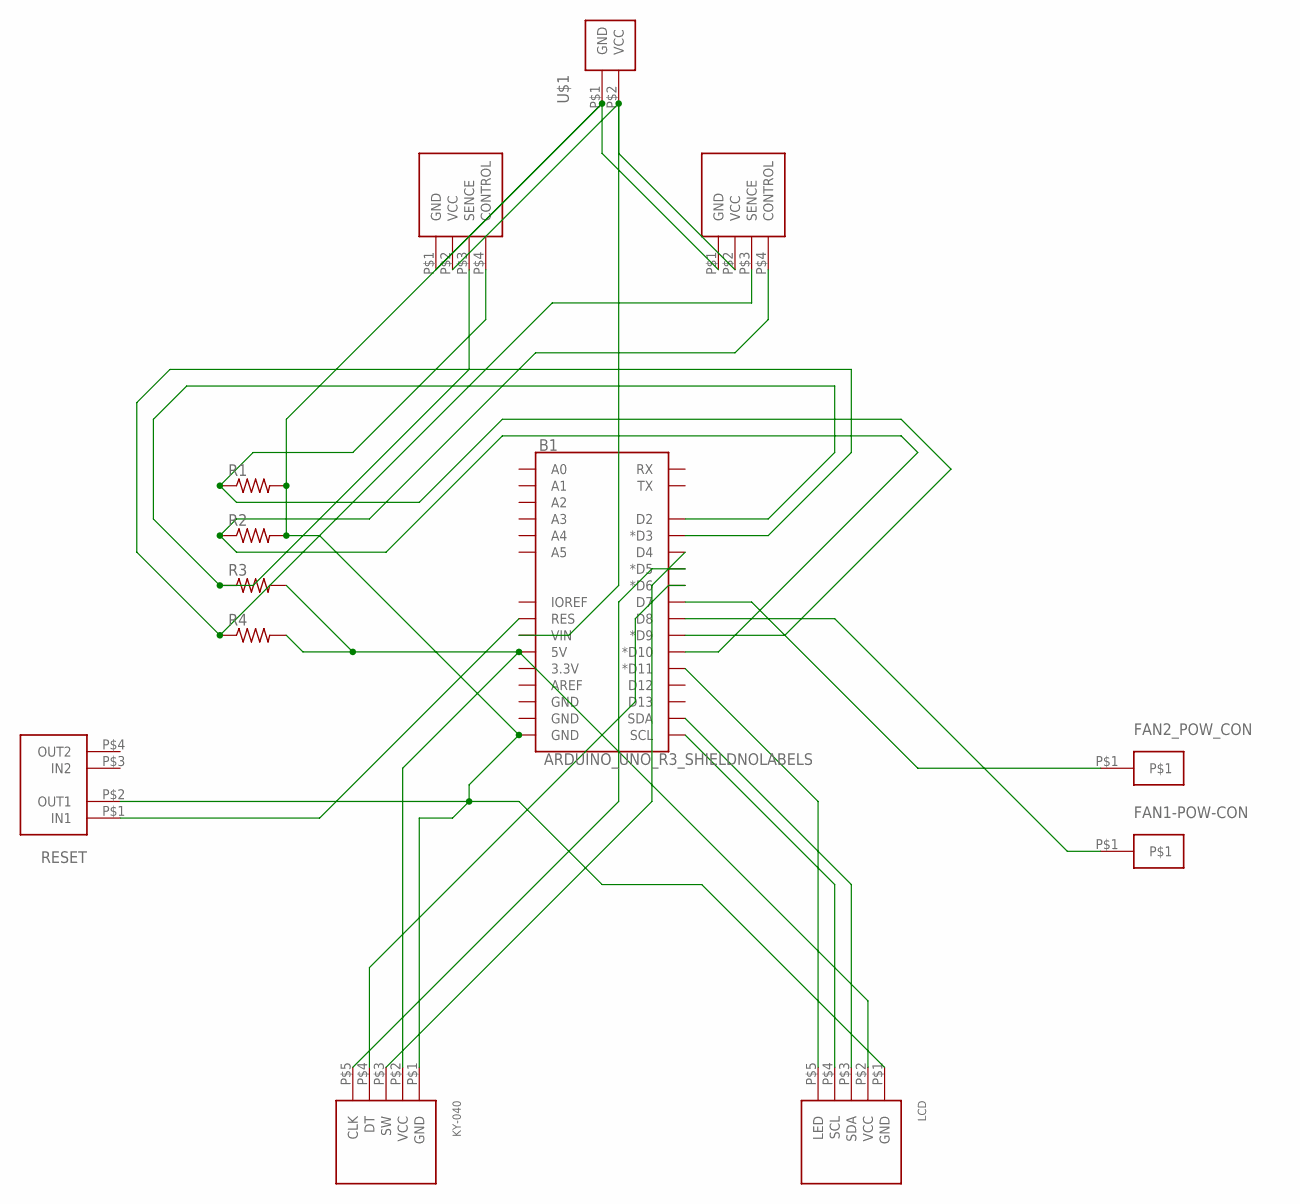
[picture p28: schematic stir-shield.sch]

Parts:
B1: ARDUINO_UNO_R3_SHIELDNOLABELS; UNO_R3_SHIELD_NOLABELS
FAN1, FAN2: 4PIN
FAN1-POW-CON, FAN2_POW_CON: 1PIN
KY-040: 5PIN_KY-04
LCD: 5PIN_LCD
R1, R2, R3, R4: FLIPFLOP-RES; 0805-THM
RESET: BUTTON
U$1: 2PIN

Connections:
unnamed: B1.D8, FAN1-POW-CON.P$1
unnamed: B1.VIN, FAN1.P$2 (VCC), FAN2.P$2 (VCC), U$1.P$2 (VCC)
unnamed: B1.D9 (*D9), FAN1.P$4 (CONTROL), R1.1
unnamed: B1.D10 (*D10), FAN2.P$4 (CONTROL), R2.1
unnamed: B1.5V, KY-040.P$2 (VCC), LCD.P$2 (VCC), R3.2, R4.2
unnamed: B1.D2, FAN1.P$3 (SENCE), R3.1
unnamed: B1.D3 (*D3), FAN2.P$3 (SENCE), R4.1
unnamed: B1.D11 (*D11), LCD.P$5 (LED)
unnamed: B1.D7, FAN2_POW_CON.P$1
unnamed: B1.SCL, LCD.P$4 (SCL)
unnamed: B1.SDA, LCD.P$3 (SDA)
unnamed: B1.D4, KY-040.P$3 (SW)
unnamed: B1.D6 (*D6), KY-040.P$4 (DT)
unnamed: B1.D5 (*D5), KY-040.P$5 (CLK)
unnamed: B1.GND@0 (GND), FAN1.P$1 (GND), FAN2.P$1 (GND), KY-040.P$1 (GND), LCD.P$1 (GND), R1.2, R2.2, RESET.P$2 (OUT1), U$1.P$1 (GND)
RESET: B1.RES, RESET.P$1 (IN1)

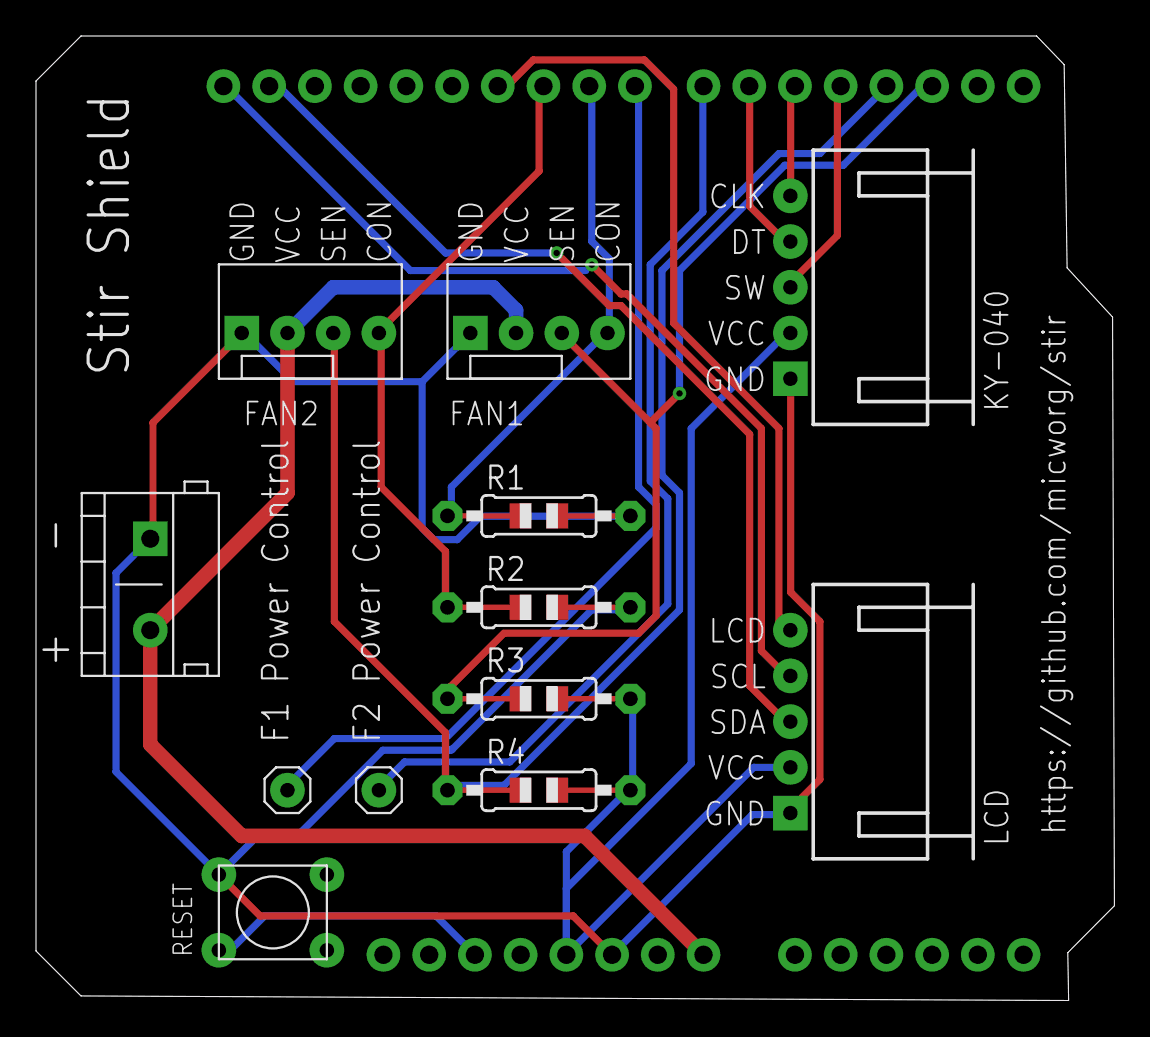
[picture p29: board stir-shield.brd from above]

Board: 2 copper layers, 59.9 x 53.6 mm, 13 parts (0 on the bottom side), 16 nets.

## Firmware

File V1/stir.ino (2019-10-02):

/////////////////////////////////////////////////////////////////////////////////////// Stir Control (mwx'2019)
#include <EEPROM.h>
#include <LiquidCrystal_I2C.h>

#define MS (long)millis()

#define SX Serial.print 
#define SXN Serial.println

String VERSION    = "1.7.3";

int SPEEDINC      = 50;                                                                // speed increment (rpm)

int FANMIN        = 200;            // fan minimum speed (should be a value at which the fan runs safely) (rpm)
int FANMAX        = 1600;              // fan maximum speed (should be the real maximum value of the fan) (rpm)

int BOFF          = 0;                                   // if set boost off will also turn the normal mode off

int BINC          = 1;                                                                 // BTIME increment (min)
int CINC          = 10;                                                                // CTIME increment (min)
int RINC          = 10;                                                                // RTIME increment (sec)
int OINC          = 3;                                                                // OTIME increment (hour)

long CATCHSTOP    = 20000;                                                       // fish catch stop period (ms)

int PWM0          = 9;                                                                    // PWM pin for 1. fan
int PWM1          = 10;                                                                   // PWM pin for 2. fan
int PWM2          = 11;                                                           // PWM pin for LCD brightness  
  
int I0            = 2;            // interrupt for fan 0 rpm signal (use 2 for Leonardo/ProMicro and 0 for Uno)
int I1            = 3;            // interrupt for fan 1 rpm signal (use 3 for Leonardo/ProMicro and 1 for Uno)
                                  
int CLK           = 5;                                                                 // clk on KY-040 encoder
int DT            = 6;                                                                  // dt on KY-040 encoder
int SW            = 4;                                                                  // sw on KY-040 encoder

int OFF0          = 7;                                                                  // off state pin 1. fan
int OFF1          = 8;                                                                  // off state pin 2. fan
int OFFSTATE      = LOW;                                                                // off state (LOW/HIGH)
                                      
long RINTERVAL    = 5000;                                                          // regulation internval (ms) 
long RDELAY       = 3000;                                                   // regulation delay on changes (ms)
int RTOL          = 8;                                                            // regulation tolerance (rpm)

long RNDINTERVAL  = 300000;                                          // randon value range change interval (ms)

long SINTERVAL    = 2000;                                                   // speed measurement internval (ms) 
int SAVERAGE      = 4;                                                             // speed measurement average 

int SAVETAG       = 1014;                                                                           // save tag 
long SAVEDELAY    = 10000;                                                            // EEPROM save delay (ms)

byte LCDB[]       = {4,8,16,24,32,64,96,128,192,255};       // LCD brightness steps (10 values, 0=off, 255=max)

byte aright[]     = {0x00,0x08,0x0C,0x0E,0x0C,0x08,0x00,0x00};                                 // LCD character
byte aup[]        = {0x04,0x0E,0x1F,0x00,0x00,0x00,0x00,0x00};
byte arnd[]       = {0x0E,0x0E,0x0E,0x00,0x00,0x00,0x00,0x00};

LiquidCrystal_I2C lcd(0x27,16,2);                                           // LCD display (connect to SDA/SCL)

int v[2],b[2],r[2]={0};double q,rpm[2]={0},xpm[2]={0},xb[2]={0},xv[2]={0},rtime[2];     // speed and regulation
long ac[2]={0},bc[2]={0};                                                              // interrupt rpm counter
long xts,sts,rts,swts,buts,savets,catts[2],stop[2],bts[2],vts[2],ots[2],rndts[2];                     // timing
int bdelay,bprocess=0,enclast,encval,M=2,S=0;                                      // button/encoder processing
int F[2],bstate[2]={0},btime[2],cat[2],ctime[2],cstate[2]={0},bclr=0,SAVE=0,LOCK=0;         // operating states
int ostate[2]={0},otime[2]={0};                                                                    // off timer
int brght;                                                                                    // LCD brightness
int rnd[2]={0},rnval[2]={0};long seed;                                                          // random speed
char form[8],out[20];String cmd[8];int icmd[8];                                                // string buffer


void setup() { ////////////////////////////////////////////////////////////////////////////////////////// SETUP  
  Serial.begin(9600);                                                                           // start serial

  lcd.init();lcd.clear();lcd.backlight();                                                     // initialize lcd
  lcd.createChar(0,aright);lcd.createChar(1,aup);lcd.createChar(2,arnd);                 // load lcd characters
  pinMode(PWM0,OUTPUT);pinMode(PWM1,OUTPUT);pinMode(PWM2,OUTPUT);                             // setup PWM pins
  pinMode(CLK,INPUT);pinMode(DT,INPUT);pinMode(SW,INPUT);                                  // setup KY-040 pins
  digitalWrite(CLK,true);digitalWrite(DT,true);digitalWrite(SW,true);               // turn ON pullup resistors
  pinMode(OFF0,OUTPUT);pinMode(OFF1,OUTPUT);                                            // setup off state pins

  attachInterrupt(I0,rpmint0,FALLING);                                           // setup interrupts vor rpm in
  attachInterrupt(I1,rpmint1,FALLING);

  TCCR1A=0;TCCR1B=0;TCNT1=0;                                                      // setup timer for 25 kHz PWM
  TCCR1A=_BV(COM1A1)|_BV(COM1B1)|_BV(WGM11);TCCR1B=_BV(WGM13)|_BV(CS10);ICR1=320;

  SAVE=0;                                                                           // load/initialize settings
  if (eer(0)!=SAVETAG) {
    for (int i=0;i<2;i++) {;v[i]=300;b[i]=700;btime[i]=30;cat[i]=0;ctime[i]=120;rtime[i]=60;F[i]=0;rnval[i]=0;}
    brght=5;seed=0;
    eew(0,SAVETAG);save();
  } else {
    for (int i=0;i<2;i++) {
      v[i]=eer(1+i);b[i]=eer(3+i);btime[i]=eer(5+i);cat[i]=eer(7+i);
      ctime[i]=eer(9+i);F[i]=eer(11+i);rtime[i]=eer(13+i);rnval[i]=eer(15+i);
    }
    seed=eer(100)+1;eew(100,seed);randomSeed(seed);
    brght=eer(101);
  }

  lset();

  enclast=digitalRead(CLK);                                                                // get encoder state

  for (int i=0;i<2;i++) catts[i]=stop[i]=vts[i]=ots[i]=rndts[i]=MS;xts=sts=rts=swts=buts=savets=MS;    // timer
  updatePWM();updatelcd();updatespeed();updatemarker();                                           // update all

  slcd(0,0,5,VERSION);                                                                          // show version
}


void loop() { //////////////////////////////////////////////////////////////////////////////////////////// LOOP

  if (Serial.available() > 0) { ////////////////////////////////////////////////////////// serial communication
    int n=cutcmd(Serial.readString());
    int err=1;
    int i=cut(icmd[1],0,1);
    if (cmd[0]=="info"    && n==1) {;err=0;}
    if (cmd[0]=="version" && n==1) {;SXN(VERSION);return;}
    if (cmd[0]=="save"    && n==1) {;save();}
    if (cmd[0]=="speed"   && n==3) {;v[i]=cut(icmd[2],FANMIN,FANMAX);err=0;}
    if (cmd[0]=="bspeed"  && n==3) {;b[i]=cut(icmd[2],FANMIN,FANMAX);err=0;}
    if (cmd[0]=="btime"   && n==3) {;btime[i]=cut(icmd[2],0,60);err=0;}
    if (cmd[0]=="ctime"   && n==3) {;ctime[i]=cut(icmd[2],60,240);err=0;}
    if (cmd[0]=="rtime"   && n==3) {;rtime[i]=cut(icmd[2],0,240);err=0;}
    if (cmd[0]=="rnval"   && n==3) {;rnval[i]=cut(icmd[2],0,1000);err=0;}
    if (cmd[0]=="on"      && n==2) {;fset(i,1);err=0;}
    if (cmd[0]=="off"     && n==2) {;fset(i,0);err=0;}
    if (cmd[0]=="bon"     && n==2) {;bset(i,1);err=0;}
    if (cmd[0]=="boff"    && n==2) {;bset(i,0);err=0;}
    if (cmd[0]=="con"     && n==2) {;cat[i]=1;catts[i]=MS;err=0;}
    if (cmd[0]=="coff"    && n==2) {;cat[i]=0;catts[i]=MS;err=0;}
    if (cmd[0]=="otime"   && n==3) {;oset(i,icmd[2]);err=0;}
    
    updatelcd();
    for (int i=0;i<2;i++) {
      SX(F[i]);SX(":");        // 0, 16  
      SX((int)(v[i]));SX(":"); // 1, 17
      SX((int)(b[i]));SX(":"); // 2, 18
      SX(rpm[i]);SX(":");      // 3, 19
      SX(xpm[i]);SX(":");      // 4, 20
      SX(r[i]);SX(":");        // 5, 21
      SX(bstate[i]);SX(":");   // 6, 22
      SX(btime[i]);SX(":");    // 7, 23
      SX(cat[i]);SX(":");      // 8, 24
      SX(ctime[i]);SX(":");    // 9, 25
      SX(rtime[i]);SX(":");    // 10, 26
      SX(otime[i]);SX(":");    // 11, 27
      SX(rnval[i]);SX(":");    // 12, 28
      SX(rnd[i]);SX(":");      // 13, 29
      if (bstate[i]) SX((((long)btime[i]*60000)-(MS-(long)bts[i]))/1000+1); else SX(0);SX(":");   // 14, 30
      if (ostate[i]) SX((((long)otime[i]*3600000)-(MS-(long)ots[i]))/1000+1); else SX(0);SX(":"); // 15, 31
    }
    SX(VERSION);SX(":"); // 32
    SX(MS);SX(":");      // 33
    SXN(err);            // 34
    save();
  }

  if (SAVE>0 && MS-savets>SAVEDELAY) {;save();SAVE=0;savets=MS;} ////////////////////// save settings if needed
  if (MS-savets>SAVEDELAY/5) bclr=1;
  
  for (int i=0;i<2;i++) {

    if (MS-rndts[i]>RNDINTERVAL) { /////////////////////////////////////////////////////////////// random timer
      rnd[i]=int(random(0,rnval[i]+1)/10)*10;rndts[i]=MS;updatelcd();
    }

    if (ostate[i] && MS-ots[i]>(long)otime[i]*3600000) { ////////////////////////////////////// check off timer
      otime[i]=0;ostate[i]=0;fset(i,0);
    }
    
    if (cat[i] && MS-catts[i]>(long)ctime[i]*60000 && F[i]==1) { //////////////////////////// initiate cat fish
      catts[i]=MS;cstate[i]=1;F[i]=0;stop[i]=MS;updatePWM();updatespeed();
    }
    
    if (cstate[i] && MS-stop[i]>CATCHSTOP && F[i]==0) { ////////////////////////// stop cat fish and start over
      cstate[i]=0;F[i]=1;vts[i]=MS;rts=MS+2000;updatePWM();updatespeed();
    }

    if (bstate[i] && MS-bts[i]>(long)btime[i]*60000) {;bstate[i]=0;S=0;updatelcd();} //////// check boost state

  }

  if (MS-xts>SINTERVAL) { /////////////////////////////////////////////////////////////////// speed measurement    
    for (int i=0;i<2;i++) xpm[i]=xpm[i]*(SAVERAGE-1)/SAVERAGE+(bc[i]/((MS-xts)/1000.0)*30.0)/SAVERAGE;
    updatespeed();xts=MS;bc[0]=0;bc[1]=0;
  }

  if (MS-rts>RINTERVAL) { //////////////////////////////////////////////////////////////////// speed regulation
    for (int i=0;i<2;i++) {
      rpm[i]=ac[i]/((MS-sts)/1000.0)*30.0;
      ac[i]=0;
      calcramp(i);
      if (!F[i]) {;r[i]=0;setPWM(i,0);}
      else {
        q=(bstate[i]?xb[i]:xv[i])-rpm[i];
        if (abs(q)>RTOL) r[i]=q<0?r[i]-1-abs(q)/10:r[i]+1+abs(q)/10;
        setPWM(i,cut((bstate[i]?xb[i]:xv[i])/(FANMAX/320.0)+r[i],0,320));
      }
    }

    sts=MS;rts=MS;
    updatespeed();
  }
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

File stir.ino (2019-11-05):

//////////////////////////////////////////////////////////////////////////////////// Stir Control V2 (mwx'2019)
#include <EEPROM.h>
#include <LiquidCrystal_I2C.h>

#define MS (long)millis()
#define NP 25                                                                 

String VERSION    = "2.1.2";

int FANINIT       = 0;                                                // initialize fan with high voltage (0/1)

int SPEEDINC1     = 20;                                                               // speed increment values
int SPEEDINC2     = 50;
int SPEEDINC3     = 100;

int SPEEDSTEP1    = 400;                           // speed increment steps (increment changes at these values)
int SPEEDSTEP2    = 1000;

int RNDINC        = 50;                                                         // random value increment (rpm)

int FANMIN        = 200;            // fan minimum speed (should be a value at which the fan runs safely) (rpm)
int FANMAX        = 2500;              // fan maximum speed (should be the real maximum value of the fan) (rpm)

int BOFF          = 0;                             // if set boost off will also turn the normal mode off (0/1)

int BINC          = 1;                                                                 // BTIME increment (min)
int CINC          = 10;                                                                // CTIME increment (min)
int RINC          = 10;                                                                // RTIME increment (sec)
int OINC          = 3;                                                                // OTIME increment (hour)

int CATCHSTOP     = 20;                                                         // fish catch stop period (sec)

int PWM0          = 9;                                                                    // PWM pin for 1. fan
int PWM1          = 10;                                                                   // PWM pin for 2. fan
int PWM2          = 11;                                                           // PWM pin for LCD brightness  
  
int I0            = 0;            // interrupt for fan 0 rpm signal (use 2 for Leonardo/ProMicro and 0 for Uno)
int I1            = 1;            // interrupt for fan 1 rpm signal (use 3 for Leonardo/ProMicro and 1 for Uno)

int SWAPENC       = 1;                                                                // swap encoder direction
                                  
int CLK           = 5;                           // clk on KY-040 encoder (swap clk and dt to invert direction)
int DT            = 6;                                                                  // dt on KY-040 encoder
int SW            = 4;                                                                  // sw on KY-040 encoder

int R0            = 7;                                                               // voltage select relais 0
int R1            = 8;                                                               // voltage select relais 1
int RTHRES        = 700;                                                      // voltage switch threshold (rpm)
                                      
int RINTERVAL     = 50;                                                            // regulation internval (ds) 
int RDELAY        = 30;                                                     // regulation delay on changes (ds)
int RTOL          = 8;                                                            // regulation tolerance (rpm)

int RNDINTERVAL   = 300;                                            // randon value range change interval (sec)
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

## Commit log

2019-02-22 added cad files
    [magnetmount.scad, magnetmount.stl]
2019-03-04 bug fixes, updated cad file
    [magnetmount.scad, magnetmount10.stl, magnetmount20.stl, magnetmount30.stl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]
2019-04-30 added case files from Jens
    [Bodenplatte_V1.1.stl, Bohrschablone_LCD Blende.stl, Frontblende.stl, KY040_Knopf.stl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]
2019-04-30 reordered CAD directory
    [magnetmount.scad, magnetmount10.stl, magnetmount20.stl, magnetmount30.stl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]
2019-04-30 added bezel files from Herbert
    [LCD -Einbaurahmen für Blende mit Encoder.stl, LCD -Einbaurahmen für Blende mit Encoder_50 mm.stl, LCD 1602_Blende mit Rahmen_Encoder links.stl, LCD 1602_Blende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]
2019-05-12 added UNO shield
    [stir-shield.brd, stir-shield.sch]
2019-09-17 updated cad files
    [Magnetaufnahme Rührer Wing3_V2.0.stl, Magnetaufnahme Rührer Wing3_V3.0.stl, Magnetaufnahme Rührer Wing3_V4.0.stl]
2019-09-28 updated support files
    [Magnetaufnahme Rührer Wing3_V2.0.stl]

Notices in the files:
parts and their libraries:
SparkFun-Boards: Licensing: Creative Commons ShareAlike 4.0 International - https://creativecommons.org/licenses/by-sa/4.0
